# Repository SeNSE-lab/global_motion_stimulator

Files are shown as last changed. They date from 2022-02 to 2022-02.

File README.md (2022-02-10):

# Global Motion Stimulator

---

The Global Motion Stimulator is a tool for stimulating the whisker array of head fixed
rodents. The stimulator can traverse the array in any direction with a range of controllable speeds,
while an optical detector senses the duration of whisker contact. For more details see
Dorizan et al, **Journal of Neuroscience Methods 2022**.

---

## Hardware Assembly
- A model for the fully assembled device can be found [here](/3D_models/assembly)
- The BOM for all purchased parts can be found [here](/docs/BOM.xlsx)
- The designs for all 3D printed parts can be found [here](/3D_models/parts)
  - All parts were printed with PLA on an Ultimaker Pro 3
- The acrylic inserts were laser-cut from 1/4" clear acrylic. They have an outer
diameter of 3.25 mm. The tapered hole to hold the nitanol bar created was created using the
laser cutter on a lower setting
- A threaded 8mm aluminum rod is used to mount the device on a micro-manipulator with a M4 bolt
- Additional holes must be drilled in the encoder mounting in order to secure it to the stepper motor
It may be advisable to wrap in tape for better grip
- A circuit diagram can be found [here](/docs/schematic.pdf)
- The motor shield user manual can be found [here](https://learn.adafruit.com/adafruit-motor-shield-v2-for-arduino)
  - Note the two Adafruit motor shields are stacked, the bottom configured to use the same
power source as the Arduino Mega, and the top to use its own source
- The fiber optic user manual can be found [here](https://www.bannerengineering.com/us/en/products/part.87591.html). A 10 kOhm load
was used

---

## Software

### Arduino

#### Installation
- This project uses a modified 
[Adafruit Motor Shield Library](https://learn.adafruit.com/adafruit-motor-shield-v2-for-arduino/install-software) 
which can be found in the [arduino/libraries](/arduino/libraries) folder in this project. It is reccomended that you install 
the library using the instructions on the [Adafruit website](https://learn.adafruit.com/adafruit-motor-shield-v2-for-arduino/install-software) then 
replace the .h and .cpp files with the ones contained in this project. This allows you to automatically install all 
dependancies (select "Install All" when using the library manager to install automatically)
  - The library typically installs either in Program Files (x86)/Arduino/libraries or Documents/Arduino/libraries
- Ensure you alter the paths at the top of the `main_slider_control.ino` script to reflect the correct
local locations for the `data_struct_lib.ino` and `timer_lib.ino` files

### Python

#### Required libraries
- pyserial
- pandas
- matplotlib

#### Instructions
`sliderlib.py` contains the main functionality for controlling the global motion stimulator device. 
Documentation can be found in comments or [here](/docs/sliderlib_documentation.pdf) 
Two example jupyter notebooks are provided with instructions in the notebooks for controlling the device. 
The `calibration_notebook` is used to assist in calibrating speeds for each angle, though calibrations should 
be verified with slider data recorded from the data acquisition system. The experiment notebook is to be used 
when running experiments.

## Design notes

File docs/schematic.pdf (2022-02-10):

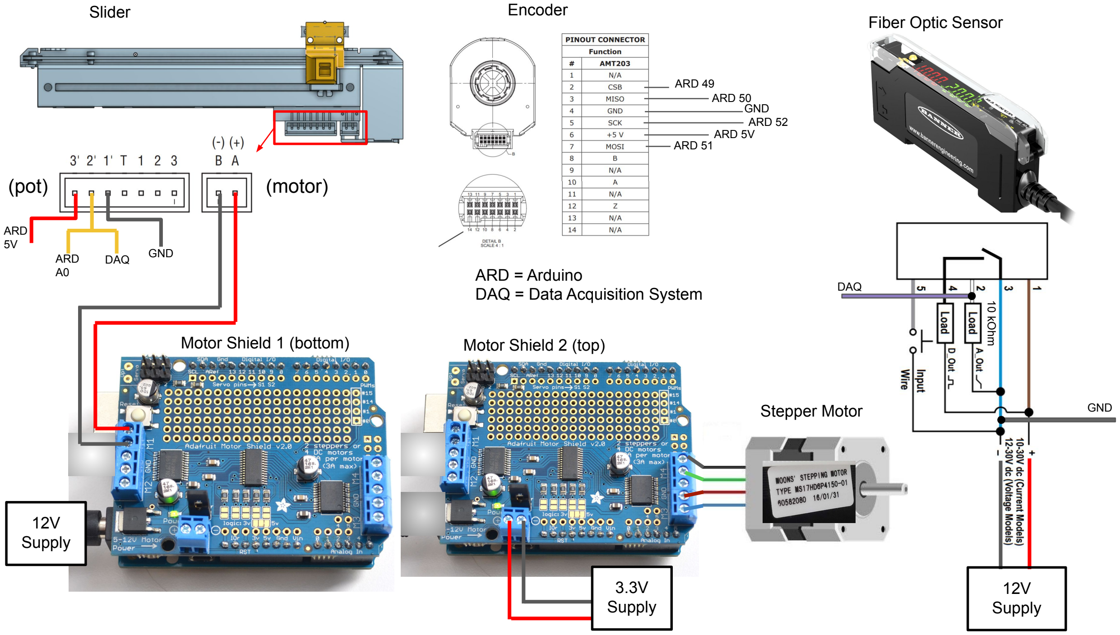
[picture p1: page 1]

ARD = Arduino
DAQ = Data Acquisition System
Slider | Encoder

ARD
5V
ARD
A0

DAQ GND

ARD 49
ARD 50
GND
ARD 52
ARD 5V
ARD 51

DAQ

12V
Supply

Fiber Optic Sensor

Motor Shield 1 (bottom)

(pot) | (motor)

12V
Supply

Stepper Motor

Motor Shield 2 (top)

3.3V
Supply

GND

10 kOhm

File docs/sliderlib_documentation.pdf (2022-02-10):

1/31/2020 | Welcome to Arduino_Slider’s documentation! — Arduino_Slider documentation
file:///C:/Users/guru/Code/Arduino_Slider/docs/build/html/index.html | 1/3

# Welcome to Arduino_Slider’s documentation!

This library contains an API for interacting with an Arduino microcontroller loaded with firmware to move a rotating slider.

sliderlib.get_datetime_str()
returns current datetime as a string with format yyyy-mm-dd-HH-MM-SS

Returns: returns current datetime as a string with format yyyy-mm-dd-HH-MM-SS sliderlib.get_time_str()
returns current time as a string with format HH-MM-SS

Returns: returns current datetime as a string with format HH-MM-SS

sliderlib.load_mapping(name, directory='mappings')
returns the mapping ‘name’ stored in ‘directory’ just a wrapper around pickle load

Parameters: name –
directory –
Returns:

sliderlib.store_mapping(d, name=None, directory='mappings') stores mapping as a pickle file just a wrapper around pickle dump

Parameters: d – mapping dictionary
name – name of mapping
directory – directory to store mapping Returns:

class sliderlib.SliderController(mapping=None, angle_order=None, dest_folder=None, animal_name=None, exp_tag=None, cell_id=None, title_string=None)
__init__(mapping=None, angle_order=None, dest_folder=None, animal_name=None, exp_tag=None, cell_id=None, title_string=None)
create slider object, connect to Arduino

Parameters: mapping – mapping between slider angle and desired speed
angle_order – order to iterate through angles dest_folder – folder to store generated data files
animal_name – identifier for animal
exp_tag – tag to identify experiment (eg ‘slow’)
title_string – custom title string to replace default naming convention of name_tag_dateTime
add_note(note, index=-1)
add a note to ‘notes’ column of data, saves changes

Parameters: note – text note to add
index – trial to which note should be added. default is to add to last trial run Returns:
analyze_test_log()
print fwd and bwd mean velocity and stdev for each angle/motor_speed combination that was tested

Returns:
engage_stepper()

file:///C:/Users/guru/Code/Arduino_Slider/docs/build/html/index.html | 2/3

send command to Arduino that will engage the stepper motor

Returns:
init()
move stepper motor to first angle, set slider to move forward next

Returns:

move_slider(speed=None, num_slides=0, log=True)
move slider to other end of track, writes new data to file after each time slider is moved

Parameters: speed – (optional) speed with which to move, if None passed in uses mapped speed num_slides – number of round trips slider should make (pass in 0 to just move to other end of track) log – (bool) add slides to log

Returns:
move_stepper_to(pos)
move stepper to nearest possible angle to specified angle

Parameters: pos – angle in degrees
Returns:
print_slider_pos()
use sparingly, high error rate query Arduino for current slider position and print to screen

Returns:
print_stepper_pos()
print full stepper info to screen, commanded position, real position, and current step number

Returns:

run_all(num_slides)
iterate through all angels in angle_order and move slider num_slides number of times (round trips)

Parameters: num_slides – number of round trips slider will make at each angle
Returns:
send_cmd(cmd)
send string command to Arduino

Parameters: cmd – (string) command to send Returns:
set_angle_idx(idx=0)
go to angle at idx in angle_order

Parameters: idx – index of desired angle in angle order
Returns:
stepper_next(deg=None)
move stepper to next angle in angle_order if an angle is passed in, stepper will rotate forward that number of degrees

Parameters: deg – (optional and not recommended) move stepper forward this many degrees
Returns:
stepper_prev(deg=None)

file:///C:/Users/guru/Code/Arduino_Slider/docs/build/html/index.html | 3/3

move stepper to previous angle in angle_order if an angle is passed in, stepper will rotate backward that number of degrees

Parameters: deg – (optional and not recommended) move stepper backward this many degrees
Returns:

store_test_log(title=None, dest_folder=None)
write test log to file defaults to prepending ‘testLog_’ to standard title and storing in standard data directory just a wrapper around pickle dump
Parameters: | title – (optional) name of test_log file
| dest_folder – directory in which to store test_log
Returns:

test_all(num_slides=5)
runs test_slider speed for all angles using current speed mapping errors a lot, may be better off running one at a time then resetting everything

Parameters: num_slides – number of slider round trips to take at each angle
Returns:

test_slider_speed(motor_speed=150, num_trials=1)
NOTE: this fails a lot after the angle is changed. also fails if slider stalls.
all successful slides were recorded, you may still analyze these. start new session to clear error.

record the average speed of the slider through the middle third of the track in meters per second call analyze_test_log() to print average speeds to screen

Parameters: | motor_speed – value 0 - 255
| num_trials – number of round trips slider should take
Returns: | timestamps_fwd, pos_fwd, timestamps_bck, pos_bck, f_speed, b_speed from last trial

write_data_to_csv(file_path=None)
write trial log to file (note this is called anytime the slider is moved or a note is added) if no argument is passed, will store using values passed in when object was created:

dest_folder/animalName_expTag_dateTime.scv
Parameters: file_path – full path (including file name) to write data
Returns:

# Indices and tables

Index
Module Index
Search Page

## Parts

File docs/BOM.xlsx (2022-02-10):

Category | Quantity | Description | Manufacturer | Model No.
Devices
 | 1 | Arduino MEGA 2560 | Arduino | A000067
 | 2 | Adafruit Motor/Stepper/Servo Shield for Arduino v2 Kit - v2.3 | Adafruit | 1438
 | 1 | Absolute Position Rotary Encoder 4096PPR/12BIT | CUI Devices | AMT203-V
 | 1 | NEMA17 Stepper Motor 2 phase, 1.8° | MOONS' | MS17HD6P4150
 | 1 | PSM Series Motorized Slide Potentiometer | Bourns Inc. | PSM01-082A-103B2
 | 1 | DF-G3 Series Long Range Fiber Optic Amplifier | Banner Engineering | DF-G3-NU-2M
Cables/Connectors
 | 1 | XH 2.5 Connector Housing 2POS | JST Sales America Inc. | XHP-2
 | 1 | XH 2.5 Connector Housing 7POS | JST Sales America Inc. | XHP-7
 | 5 | XH 2.5 Connector Socket 22-28AWG CRIMP | JST Sales America Inc. | SXH-001T-P0
 | 1 | Rectangular Cable Assemblies Double Row Discrete Wire Assembly, 0.050 Pitch | Samtec | SFSD-07-28-G-10.00-S
 | 1 | General Purpose Fiber Optic Cable, Through Beam, 6 9/16 ft Cable Length | Omron | E32-TC200A
 | 10 | Mini-PV ("DuPont") Connectors (Various)
 | 1 | Power Cord 12v Barrel Plug, 2.1mm I.D. x 5.5mm O.D. x 10.0mm
 | 2 | DAQ Connection Cables (Typically BNO)
Hardware
 | 1 | Universal Aluminum Mounting Hub for 5mm Shaft, M3 Holes | Pololu | 1998
 |  | M3 Hardware (Various)
 | 1 | M4 Bolt
Materials
 | 1 | Nitinol Wire .01 in Diameter
 | 1 | Clear Acryllic Sheet .25 in
 | 1 | Aluminum Rod 8 mm dia x 100 mm

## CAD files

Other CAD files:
3D_models/parts/fo_mount.sldprt
3D_models/parts/track_to_stepper_mount.sldprt
3D_models/parts/fork.sldprt
3D_models/parts/fork_to_track_mount.sldprt
3D_models/parts/fo_strain_relief.sldprt
3D_models/parts/stepper_to_rod_mount.sldprt
3D_models/parts/fo_mount.stl
3D_models/parts/fo_strain_relief.stl
3D_models/parts/fork.stl
3D_models/parts/fork_to_track_mount.stl
3D_models/parts/stepper_to_rod_mount.stl
3D_models/parts/track_to_stepper_mount.stl

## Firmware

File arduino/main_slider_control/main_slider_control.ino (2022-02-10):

#include <Wire.h>
#include <SPI.h>
#include <Adafruit_MotorShield.h>
#include "utility/Adafruit_MS_PWMServoDriver.h"
#include "C:\Users\user\global_motion_stimulator\arduino\libraries\timer_lib\timer_lib.ino"
#include "C:\Users\user\global_motion_stimulator\arduino\libraries\data_struct_lib\data_struct_lib.ino"


#define RETRACT_SPEED 180

#define MOVEMENT_TRIGGER 1
#define TRIGGER_PIN A3
#define MOTOR_SHAFT_FACING_AWAY 0
#define LED_PIN 31

#define DEBUG_MESSAGES 1
#define SAMPLING_EPOCHS 5
#define DEBUG_ONLY 0
// 60 100
#define HOLD_PWM 60   // motor can tolerate about 3V when holding, power is about 12 V  (3/12) * 255 ~= 60
#define MOVE_PWM 100   // 4.7 V

#define CS 49 //Chip Select 

#define ENC_ZERO 90.72
#define STEP_DEG 0.9


// Create the motor shield object with the default I2C address
Adafruit_MotorShield AFMS = Adafruit_MotorShield();
Adafruit_MotorShield AFMS2 = Adafruit_MotorShield(0x61);


// Select which 'port' M1, M2, M3 or M4. In this case, M1
Adafruit_DCMotor *slider_motor = AFMS.getMotor(1);

// Stepper motor object
Adafruit_StepperMotor *direction_motor;

bool debug = true;


int slider_readout = A0;
int STEPS_PER_REVOLUTION = 400;
int state = 0;
int test_stepper = 0;

int current_steps = 0;

// Number of words (argument variables) in a user command line.
char *argument_words[8];
// Buffer to use for receiving special user-defined ASCII commands.
char user_command_buffer[64];
// Index to use when filling the user command buffer.
uint8_t user_command_buffer_index = 0;
uint8_t c = 0;  // character received

char output_line[71];

int read_percent_track = 0;
int set_percent_track = 0;
uint8_t set_speed = 170;   // 0-255

int degrees_to_move = 0;
int direction_to_move = 0;
int step_size = 0;
int current_degrees = 0;

unsigned int slider_buffer_size = 250;
circular_buffer_int *slider_buffer;

unsigned long timestamps[200];
int time_idx = 0;
//unsigned int timestamp_buffer_size = 250;
//circular_buffer_int *timestamp_buffer;

boolean last_led_state = 1;
uint8_t timed_function2;

volatile boolean print_message_timed;
volatile unsigned long times_in_isr = 0;
timed_function *sampling_timer;
sampled_time *sampled_times[SAMPLING_EPOCHS];
uint8_t sample_time_index = 0;
volatile boolean stamp_first = false, stamp_last = false;
unsigned long sampling_period = 1333;  // in microseconds.
unsigned long timer_frequency = 750;      // in Hz.
unsigned long last_trial_time = 0;

// Session parameters
unsigned int orientations[8] = {0, 45, 90, 135, 180, 225, 270, 315};
unsigned int orientation = 0;
unsigned int last_orientation = 0;
boolean in_trial = false;
boolean run_trial = false;
int minimum_position = 30;
int maximum_position = 70;

// Trial parameters.
unsigned int trial_number = 0;
unsigned int inter_trial_interval = 3000; // milliseconds.
uint8_t slider_speed = 160;
int starting_position = 15;
int ending_position = 50;

// Trial results
unsigned long start_trigger_timestamp_us;
unsigned long stop_trigger_timestamp_us;

uint8_t SPI_T (uint8_t msg)    //Repetive SPI transmit sequence
{
  uint8_t msg_temp = 0;  //vairable to hold recieved data
  digitalWrite(CS, LOW);    //select spi device
  msg_temp = SPI.transfer(msg);    //send and recieve
  digitalWrite(CS, HIGH);   //deselect spi device
  return (msg_temp);     //return recieved byte
}


float read_encoder(bool proc = true) {
  // adapted from http://myrobotlab.org/content/code-cui-amt203-absolute-encoder
  // absolute position in deg

  // do a dummy read to clear old data
  if (proc) {
    read_encoder(false);
  }
  uint8_t recieved = 0xA5;    //just a temp vairable (encoder idle)
  uint8_t temp[2];
  short pos = 0;
  uint8_t count = 0;

  SPI.begin();    //start transmition
  digitalWrite(CS, LOW);

  SPI_T(0x10);   //issue read command

  recieved = SPI_T(0x00);    //issue NOP to check if encoder is ready to send

  while (recieved != 0x10)    //loop while encoder is not ready to send
  {
    recieved = SPI_T(0x00);    //cleck again if encoder is still working
    delay(2);    //wait a bit

    // If fails too many times,send read command again
    if (count > 7 && recieved != 0x10) {
      recieved = SPI_T(0x10);
      delay(2);
      count = 0;
    }

    count++;
  }

  temp[0] = SPI_T(0x00);    //Recieve MSB
  temp[1] = SPI_T(0x00);    // recieve LSB

  digitalWrite(CS, HIGH); //just to make sure
  SPI.end();    //end transmition

  temp[0] &= ~ 0xF0;   //mask out the first 4 bits

  pos = temp[0] << 8;    //shift MSB to correct pos in pos message
  pos += temp[1];        // add LSB to pos message to complete message

  delay(20);

  return (float)(pos * 0.08789);    // aprox 360/2**12
}

void parse(char *line, char **argument_words, uint8_t maxArgs) {
  uint8_t argCount = 0;
  while (*line != '\0') {       /* if not the end of line ....... */
    while (*line == ',' || *line == ' ' || *line == '\t' || *line == '\n')
      *line++ = '\0';     /* replace commas and white spaces with 0    */
    *argument_words++ = line;          /* save the argument position     */
    argCount++;
    if (argCount == maxArgs - 1)
      break;
    while (*line != '\0' && *line != ',' && *line != ' ' &&
           *line != '\t' && *line != '\n')
      line++;             /* skip the argument until ...    */
  }
  **argument_words = '\0';                 /* mark the end of argument list  */
}

void move_slider(int percent_of_track, uint8_t speed_of_motor, int direction_of_movement, boolean sampling) {
  // Speed range is 0-255

  //sprintf(output_line, "Moving slider: percent = %d, speed = %d, direction = %d", percent_of_track, speed_of_motor, direction_of_movement);
  //Serial.println(output_line);
  time_idx = 0;
  //  if (debug) {
  //    Serial.print("moving slider: ");
  //    Serial.print(percent_of_track);
  //    Serial.print("\tspeed: ");
  //    Serial.print(speed_of_motor);
  //    Serial.print("\tdirection: ");
  //    if (direction_of_movement == FORWARD)
  //      Serial.println("forward");
  //    else if (direction_of_movement == BACKWARD)
  //      Serial.println("backwards");
  //  }

  percent_of_track = int(10.24 * percent_of_track);

  int read_track = analogRead(slider_readout);
  if (read_track == percent_of_track)
    //Serial.println("Already there bro!");
    return;
  // Wrong direction entered
  else if ((direction_of_movement == FORWARD) && (percent_of_track < read_track)) {
    if (debug) Serial.println(F("Can't do that bro! Move backwards instead"));
  }
  else if ((direction_of_movement == BACKWARD) && (percent_of_track > read_track)) {
    if (debug) Serial.println(F("You mean move forward? We're already past that point!"));
  }
  else {
    boolean not_there_yet = true;

    // Pin to end of track before moving in commanded direction

  if (direction_of_movement == FORWARD) {
      if (read_track > 2) {
        slider_motor->setSpeed(RETRACT_SPEED);
        slider_motor->run(BACKWARD);
        while (read_track > 2) {
          read_track = analogRead(slider_readout);
        }
      }
    }
    else {
      if (read_track < 1021) {
        slider_motor->setSpeed(RETRACT_SPEED);
        slider_motor->run(FORWARD);
        while (read_track < 1021) {
          read_track = analogRead(slider_readout);
        }
      }
    }
    slider_motor->setSpeed(50);
    delay(200);



    
    slider_motor->setSpeed(speed_of_motor);
    if (sampling) {
      stamp_first = true;
      run_timed_function(sampling_timer);
      delay(25);
      if (MOVEMENT_TRIGGER) {
        digitalWrite(TRIGGER_PIN, HIGH);
        start_trigger_timestamp_us = micros();
      }
    }
    slider_motor->run(direction_of_movement);
    digitalWrite(LED_PIN, HIGH);
    while (not_there_yet) {
      //read_percent_track = analogRead(slider_readout);
      if (sampling)
        read_track = read_last_element(slider_buffer);
      else
        read_track = analogRead(slider_readout);

      if (direction_of_movement == FORWARD) {
        if (percent_of_track < read_track)
          not_there_yet = false;
      }
      else if (direction_of_movement == BACKWARD) {
        if (percent_of_track > read_track)
          not_there_yet = false;
      }
      //Serial.println(read_percent_track);
    }
  }
  // TODO HEREHERE return ! if encoder moved, else return something else
  slider_motor->run(RELEASE);
  digitalWrite(LED_PIN, LOW);

  if (sampling) {
    if (MOVEMENT_TRIGGER) {
      digitalWrite(TRIGGER_PIN, LOW);
      stop_trigger_timestamp_us = micros();
    }
    stamp_last = true;
    // delay 5 sampling periods worth to make sure last packet is printed out.
    delay(5 * 1000 / timer_frequency);
  }

  // make sure stepper didn't move during slide
  float pos = read_encoder();
  if (abs((pos - ENC_ZERO) - (float)(current_steps * STEP_DEG)) > STEP_DEG) {
    //read agian to make sure stepper didn't give anamalous reading
    pos = read_encoder();
    if (abs((pos - ENC_ZERO) - (float)(current_steps * STEP_DEG)) > STEP_DEG) {
      Serial.print('!');
      fine_tune_stepper(current_steps * STEP_DEG);
    }
    else Serial.print('1');
  }
  else Serial.print('1');




  //Serial.print("Current slider position at: ");
  //read_percent_track = analogRead(slider_readout);
  //Serial.print(read_percent_track/10.24);
  //Serial.println("%");
  return;
}

void move_stepper(int degrees_to_turn, int rotation_direction, int step_size) {

  if (debug) {
    Serial.print("moving stepper from ");
    Serial.print(current_degrees);
    Serial.print(" by ");
    Serial.print(degrees_to_turn);
    Serial.print(" degrees\tdirection: ");
    if (rotation_direction == FORWARD)
      Serial.println("clockwise");
    else if (rotation_direction == BACKWARD)
      Serial.println("counterclockwise");
  }

  if (degrees_to_turn == 0)
    return;

  int steps_number;
  float steps_per_degree;
  steps_per_degree = STEPS_PER_REVOLUTION / 360.0;
  steps_number = int(degrees_to_turn * steps_per_degree);
  if (debug) Serial.println(steps_number);
  //Serial.print("steps: ");
  //Serial.println(steps_number);
  //if(MOVEMENT_TRIGGER)
  //   digitalWrite(TRIGGER_PIN, HIGH);
  if (!MOTOR_SHAFT_FACING_AWAY) {
    if (rotation_direction == FORWARD)
      rotation_direction = BACKWARD;
    else if (rotation_direction == BACKWARD)
      rotation_direction = FORWARD;
  }
  direction_motor->step(steps_number, rotation_direction, step_size, MOVE_PWM);
  //if(MOVEMENT_TRIGGER)
  //   digitalWrite(TRIGGER_PIN, LOW);

  if (rotation_direction == FORWARD)
    current_degrees = (current_degrees + degrees_to_turn) % 360;
  else if (rotation_direction == BACKWARD)
    current_degrees = (current_degrees - degrees_to_turn) % 360;

  AFMS.setPWM(direction_motor->PWMApin, HOLD_PWM * 16);
  AFMS.setPWM(direction_motor->PWMBpin, HOLD_PWM * 16);
}

void engage_stepper(void) {
  float pos = read_encoder();
  int steps_number;
  float deg_to_turn;
  if (pos > 230) {
    deg_to_turn = ENC_ZERO + (360 - pos);
    steps_number = (int)(deg_to_turn / STEP_DEG);
    direction_motor->step(steps_number, FORWARD, INTERLEAVE, MOVE_PWM);
  }
  else if (pos < ENC_ZERO) {
    deg_to_turn = ENC_ZERO - pos;
    steps_number = (int)(deg_to_turn / STEP_DEG);
    direction_motor->step(steps_number, FORWARD, INTERLEAVE, MOVE_PWM);
  }
  else {
    deg_to_turn = pos - ENC_ZERO;
    steps_number = (int)(deg_to_turn / STEP_DEG);
    direction_motor->step(steps_number, BACKWARD, INTERLEAVE, MOVE_PWM);
  }
  fine_tune_stepper(0);
  current_steps = 0;
}

void fine_tune_stepper(float target_deg) {
  float pos = read_encoder();
  float target_enc = target_deg + ENC_ZERO;

  while (pos - target_enc > .9) {
    direction_motor->step(1, BACKWARD, INTERLEAVE, MOVE_PWM);
    delay(50);
    pos = read_encoder();

  }
  while (pos - target_enc < -.9) {
    direction_motor->step(1, FORWARD, INTERLEAVE, MOVE_PWM);
    delay(50);
    pos = read_encoder();
  }

  AFMS.setPWM(direction_motor->PWMApin, HOLD_PWM * 16);
  AFMS.setPWM(direction_motor->PWMBpin, HOLD_PWM * 16);
}
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

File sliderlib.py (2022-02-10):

# TODO measure travel distance
# TODO check move slider/test slider to make sure forward/backward mapping properly

"""
This library contains an API for interacting with an Arduino microcontroller loaded with firmware to move a rotating
slider.
"""

import serial
import serial.tools.list_ports
import datetime
import time
import os
import pickle
import struct
import pandas as pd
import warnings
import statistics

BAUD_RATE = 115200
STEPS_PER_REVOLUTION = 400
FORWARD = 1
REVERSE = 0
DIR_STR = {1: 'f', 0: 'b'}
KEY_LIST = ['start_time', 'end_time', 'stepper_ang', 'cmd_speed', 'direction', 'result', 'notes']


class SliderController(object):
    def __init__(self, mapping=None, angle_order=None, dest_folder=None,
                 animal_name=None, exp_tag=None, cell_id=None, title_string=None):
        """
        create slider object, connect to Arduino

        :param mapping: mapping between slider angle and desired speed
        :param angle_order: order to iterate through angles
        :param dest_folder: folder to store generated data files
        :param animal_name: identifier for animal
        :param exp_tag: tag to identify experiment (eg 'slow')
        :param title_string: custom title string to replace default naming convention of name_tag_dateTime
        """

        # initialize variables
        self.mapping = mapping
        self.angle_order = angle_order
        self.date_time_str = get_datetime_str()

        if not dest_folder:
            dest_folder = os.getcwd()
        self.dest_folder = dest_folder
        try:
            assert(os.path.isdir(self.dest_folder))
        except:
            raise IsADirectoryError('destination directory is not valid:\t' + self.dest_folder)

        if not title_string:
            if not animal_name:
                animal_name = 'noAnimalName'
                warnings.warn('no animal name specified')
            if not exp_tag:
                exp_tag = 'noExpTag'
                warnings.warn('no experiment tag specified')
            if cell_id is None:
                cell_id = 'noCellID'
                warnings.warn('no cell ID specified')
            cell_id = str(cell_id)
            title_string = animal_name + '_' + exp_tag + '_' + cell_id + '_' + self.date_time_str
        self.title_string = title_string

        # check to make sure each angle_order is mapped
        if angle_order:
            for a in self.angle_order:
                if a not in self.mapping.keys():
                    warnings.warn('There is an angle in angle_order with no speed mapped: ' + str(a))

        self.last_time = 0
        self.delay = .5

        self.angle_idx = -1

        self.dir = FORWARD
        self.cmd_pos = 0
        self.real_pos = 0
        self.steps = 0

        self.test_log = {}

        self.log = pd.DataFrame(columns=KEY_LIST)
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
